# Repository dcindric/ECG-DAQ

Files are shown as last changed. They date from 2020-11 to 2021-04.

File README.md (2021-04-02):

# ECG-DAQ

<p align="justify">

ECG-DAQ is the data acquisition system for electrocardiogram signals. This project is built from scratch meaning that all that schematics and PCB is made by myself based on the reference designs, simulations and laboratory testing on prototypes. 

PCB is logically/phisically divided into two parts - precision analog section where input signals, coming from the electrodes (left and right arm, right leg), are conditioned and digital section used for signal processing and data transmission. 

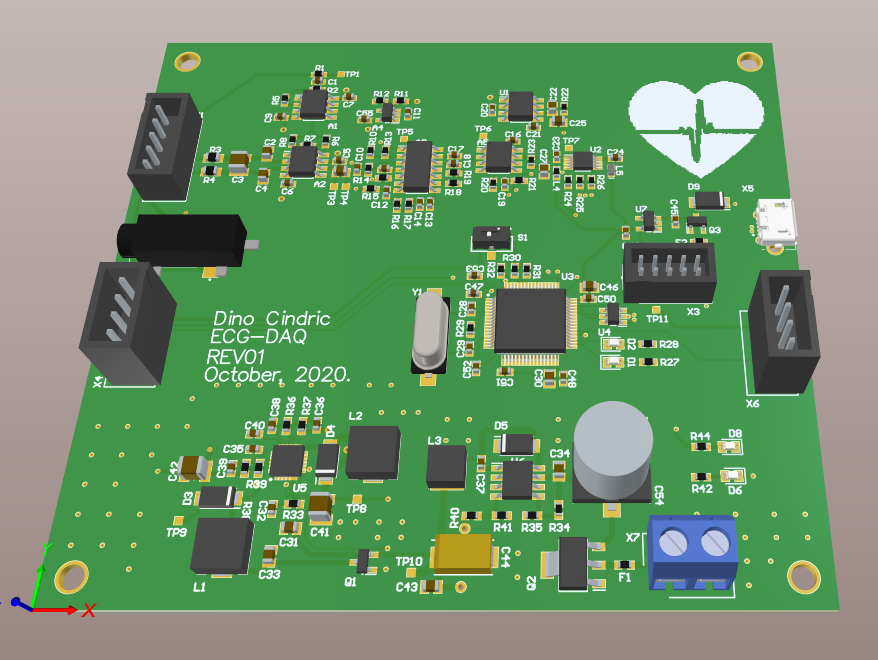
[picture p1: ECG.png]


Input signal conditioning includes:
* RFI/EMI differential filtering
* First gain stage using instrumentation amplifier INA818
* High-pass filtering implemented with 1st order C-R network 
* Second gain stage
* 5th order active Butterworth low-pass filter
* Precision ADC input preconditioning - voltage follower + antialiasing filtering
* ADCs voltage reference with driver circuit

Digital section is based on STM32F407 MCU and it's used for acquiring signals from ADC using 3-Wire SPI protocol, USB, I2C and UART communication with external devices and for executing various signal processing algorithms on acquired data (e.g. Pan-Tompkins). 

</p>

## Usage

Project files, including schematic and PCB documents, need to be opened with Altium Designer. Gerber files are production-ready and can be reviewed with various free alternative tools. 

**Disclaimer**: This project is work in progress. Use the files, hardware, and software given in this repository at your own risk.

## Updates
 * With power supply section completely soldered, negative voltage at TPS65130 regulator gave unstable, pulsating voltage, from -19 V up to -4 V.  The main reason for that behavior is that noise coupled into negative feedback pin (FBN) can be too large. This type of problem is well known for  this specific regulator and the solution is to add 51k resistor between C29 (16pF) capacitor and negative voltage rail. More discussion about this can be found here:
	* https://e2e.ti.com/support/power-management/f/power-management-forum/750348/tps65130-negative-supply-of-the-tps65130-is-not-regulating
	* https://e2e.ti.com/support/power-management/f/power-management-forum/727069/tps65130-inverting-converter-is-not-regulating-under-load
 * For some reason, I've received ADC's voltage reference driver opamp OPA2350 in wrong footprint. On the current prototyping board I've decided to solder TLV2376 opamp instead of OPA2350, since it's specifications should be good enough for ADC's voltage reference driver.
 * Initial testing of so-far-assembled board (only MCU section is not soldered yet) gave promising results.  More detailed test will be done after complete board assembly - basic functionalities of analog section are tested (signal amplification, filtering) and do perform well. Currently assembled parts of the board can be seen on the picture below.

**NOTE:** All component values and designators refer to ECG-DAQ schematic version 1.0, which can be found in Hardware/ProjectOutputs directory of this project.

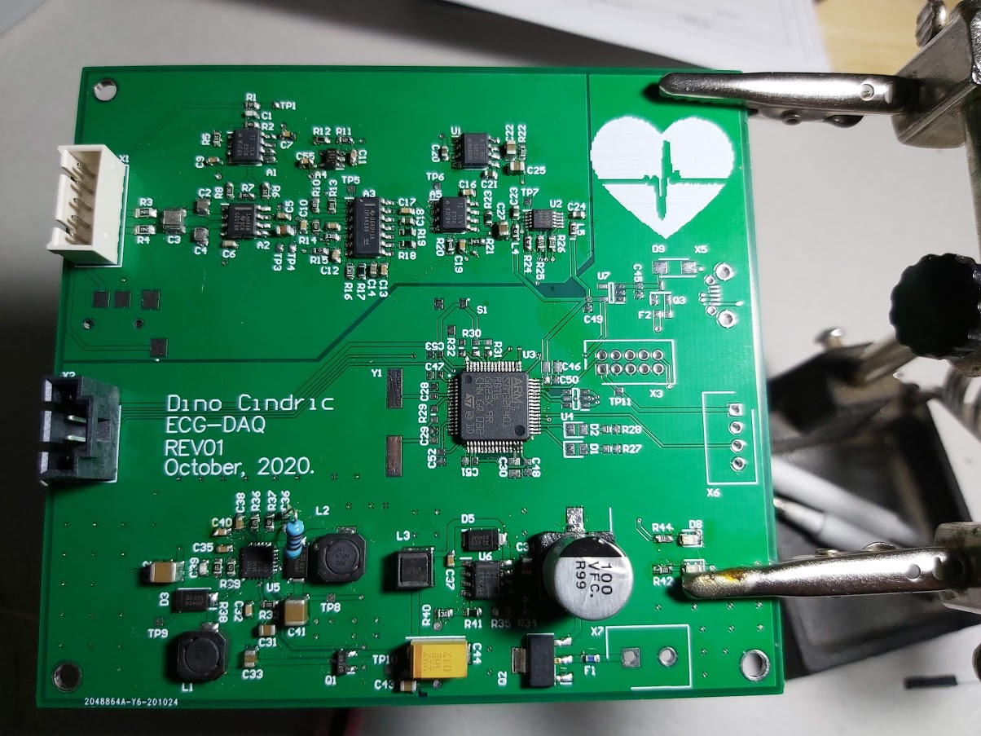
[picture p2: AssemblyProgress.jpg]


## Contributing
I'm currenlty writing firmware for the made PCB. It is very likely that there will be several versions of this project, so for any major or minor changes you would like to implement yourself, please open an issue so we can discuss about it or alternatively send me an email: dino.cindric@fer.hr.

Thank you.

## License
[MIT](https://choosealicense.com/licenses/mit/) Copyright (c) 2020, Dino Cindrić - All rights reserved.

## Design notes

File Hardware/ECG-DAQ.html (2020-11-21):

Altium customize

# Board Information Report

Date: | | 10/18/2020
Time: | | 4:13:02 PM
Elapsed Time: | | 00:00:00
Filename: | | C:\Users\Dino\Desktop\ECG Project\Schematic and PCB Design\ECG_DAQ\ECG-DAQ.PcbDoc
Units: | | mmmils

## Contents

Contents

Board Specification

General

Layer Information

Layer Information

## Board Specification

General
Board Size | 100mm x 91mm
Components on board | 146

Back to top

## Layer Information

Layer | Arcs | Pads | Vias | Tracks | Texts | Fills | Regions | ComponentBodies
Top Layer | 0 | 428 | 0 | 785 | 0 | 0 | 2 | 0
Int1 (GND) | 0 | 0 | 0 | 4 | 0 | 0 | 1 | 0
Int2 (PWR) | 0 | 0 | 0 | 4 | 0 | 0 | 1 | 0
Bottom Layer | 0 | 0 | 0 | 112 | 0 | 0 | 2 | 0
Mechanical 1 | 0 | 0 | 0 | 5 | 0 | 0 | 0 | 126
Dimensions | 0 | 0 | 0 | 16 | 2 | 0 | 0 | 0
Mechanical 13 | 0 | 0 | 0 | 570 | 0 | 0 | 0 | 10
Mechanical 15 | 0 | 0 | 0 | 542 | 0 | 0 | 0 | 0
Multi-Layer | 0 | 35 | 120 | 0 | 0 | 0 | 1 | 0
Top Paste | 0 | 0 | 0 | 0 | 0 | 0 | 0 | 0
Top Overlay | 7 | 0 | 0 | 196 | 292 | 0 | 0 | 0
Top Solder | 0 | 0 | 0 | 0 | 0 | 0 | 0 | 0
Bottom Solder | 0 | 0 | 0 | 0 | 0 | 0 | 0 | 0
Bottom Overlay | 0 | 0 | 0 | 0 | 0 | 0 | 0 | 0
Bottom Paste | 0 | 0 | 0 | 0 | 0 | 0 | 0 | 0
Drill Guide | 0 | 0 | 0 | 0 | 0 | 0 | 0 | 0
Keep-Out Layer | 0 | 0 | 0 | 6 | 0 | 0 | 0 | 0
Drill Drawing | 3 | 0 | 0 | 114 | 145 | 0 | 0 | 0
Total | 10 | 463 | 120 | 2354 | 439 | 0 | 7 | 136

Back to top

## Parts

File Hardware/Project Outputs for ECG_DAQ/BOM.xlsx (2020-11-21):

Comment | Designator | Quantity | Manufacturer Part Number 1
TLV2376IDR | A1 | 1 | TLV2376IDR
INA818IDR | A2 | 1 | INA818IDR
OPA4188IDR | A3 | 1 | OPA4188AIDR
OPA1671 | A4 | 1 | OPA1671IDBVR
OPA2350EA/2K5 | A5 | 1 | OPA2350EA/2K5
68p | C1 | 1 | C0603C680M5HACTU
680p | C2, C4 | 2 | ECH-U1H681GX5
22n | C3 | 1 | ECH-U1H223GX5
100n | C5, C6, C7, C9, C11, C12, C14, C15, C16, C18, C26, C32, C47, C48, C50, C51, C52, C53 | 18 | EMK107B7104KA-T, [NoValue]
6.8u | C8 | 1 | C2012X6S1C685M125AC
220p | C10 | 1 | VJ0603Y221KXJPW1BC
150n | C13 | 1 | CL10B154KO8NNNC
1u | C17, C20, C21, C45, C49 | 5 | EMK107BJ105KA-T
10n | C19, C35, C37 | 3 | C0603C103J4RACAUTO
10u | C22, C25, C27, C31, C33, C34, C43, C46 | 8 | EMK212BB7106KG-T
1uF | C23, C24 | 2 | EMK107BJ105KA-T
30p | C28, C29 | 2 | 06035U300FAT2A
2.2u | C30 | 1 | CL21B225KOFNNNE
16p | C36, C39 | 2 | AC0603JRNPO9BN160
220n | C38 | 1 | C0603C224J4RECTU
4.7n | C40 | 1 | C0603C472J5RACTU
22u | C41, C42 | 2 | TMK325B7226MMHP
220uF | C44 | 1 | TPSD227M016R0200V
RED | D1, D8 | 2 | LTST-C170CKT
GREEN | D2, D6 | 2 | LTST-C170KGKT
B340AF-13 | D3, D4, D5 | 3 | B340AF-13
YELLOW | D7 | 1 | LTST-C171YKT
B340A | D9 | 1
500mA | F1 | 1 | CC06FA500MA-TR
250mA | F2 | 1 | SF-0603FP025F-2
4.7uH | L1, L2 | 2 | B82462G4472M
18uH | L3 | 1 | SRR4828A-180M
SI2323DS-T1-GE3 | Q1, Q3 | 2 | SI2323DS-T1-GE3, [NoValue]
BSP321PH | Q2 | 1 | BSP321PH6327XTSA1
430k | R1, R37, R38 | 3 | CR0603-FX-4303ELF
750k | R2, R9 | 2 | CR0603-FX-7503ELF
2.4k | R3, R4 | 2 | ERJ-6ENF2401V
10k | R5, R6, R8, R14, R22, R32, R40 | 7 | RC0603FR-0710KL
4.64k | R7 | 1 | CR0603-FX-4641ELF
1k | R10 | 1 | RC0603FR-071KL
120k | R11, R36, R39 | 3 | CR0603-FX-1203ELF
100k | R12, R34, R35 | 3 | ERJ-3EKF1003V
39k | R13 | 1 | CR0603-FX-3902ELF
0Ω | R15 | 1 | ERJ-3GEY0R00V
6.34k | R16 | 1 | CRCW06036K34FKEA
9.76k | R17 | 1 | CRCW06039K76FKEA
2.43k | R18 | 1 | CRCW06032K43FKEA
3.74k | R19 | 1 | CRCW06033K74FKEA
4.7Ω | R20, R21 | 2 | CRCW06034R70FKEAC
0.1Ω | R23 | 1 | 560050316001
0Ω | R24 | 1 | ERJ-3GEY0R00V
47Ω | R25, R26 | 2 | CRCW060347R0JNEAC
2.0k | R27 | 1 | CRCW06032K00FKEA
1.8k | R28, R42, R43 | 3 | CRCW060311K8FKEA
47Ω | R29 | 1
4.7k | R30, R31 | 2 | CRCW06034K70FKEA
100Ω | R33 | 1 | CRCW0603100RFKEAC
3.24k | R41 | 1 | CRCW06033K24FKEA
2k | R44 | 1 | CRCW06032K00FKEA
CJS-1200TB | S1 | 1
REF5050 | U1 | 1 | REF5050AIDR
ADS8866IDGSR | U2 | 1 | ADS8866IDGSR
STM32F401RBT6 | U3 | 1 | STM32F401RBT6
USBLC6-2SC6 | U4 | 1 | USBLC6-2SC6
TPS65130 | U5 | 1 | TPS65130RGER
TPS5430DDAR | U6 | 1 | TPS5430DDAR
NCP115ASN330T2G | U7 | 1 | NCP115ASN330T2G
Pin Header | X1 | 1 | 35312-0560
3.5mm jack | X2 | 1 | SJ2-3574A-SMT-TR
SWD_CONN | X3 | 1 | 87831-1019
I2C_CONN | X4 | 1 | 171971-0004
USB Micro B | X5 | 1
UART_CONN | X6 | 1 | 171971-0004
VIN | X7 | 1 | 691111710002
8 MHz | Y1 | 1 | ECS-080-18-5PX-JES-TR

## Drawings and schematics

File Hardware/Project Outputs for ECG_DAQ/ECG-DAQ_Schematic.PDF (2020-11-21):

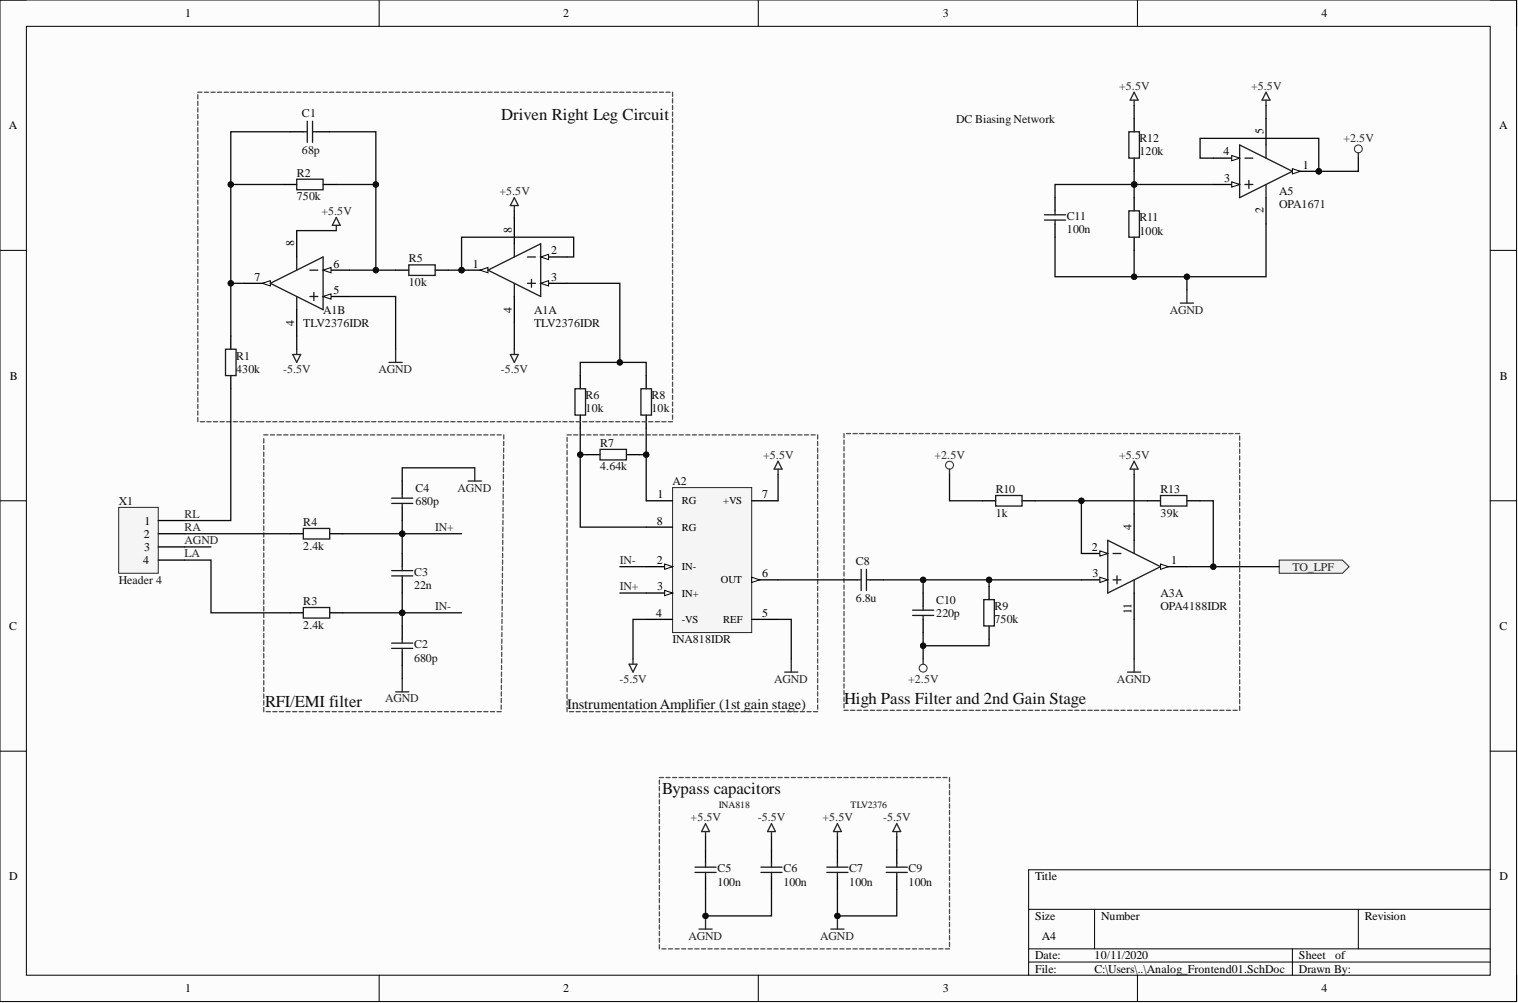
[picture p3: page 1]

Driven Right Leg Circuit

High Pass Filter and 2nd Gain Stage

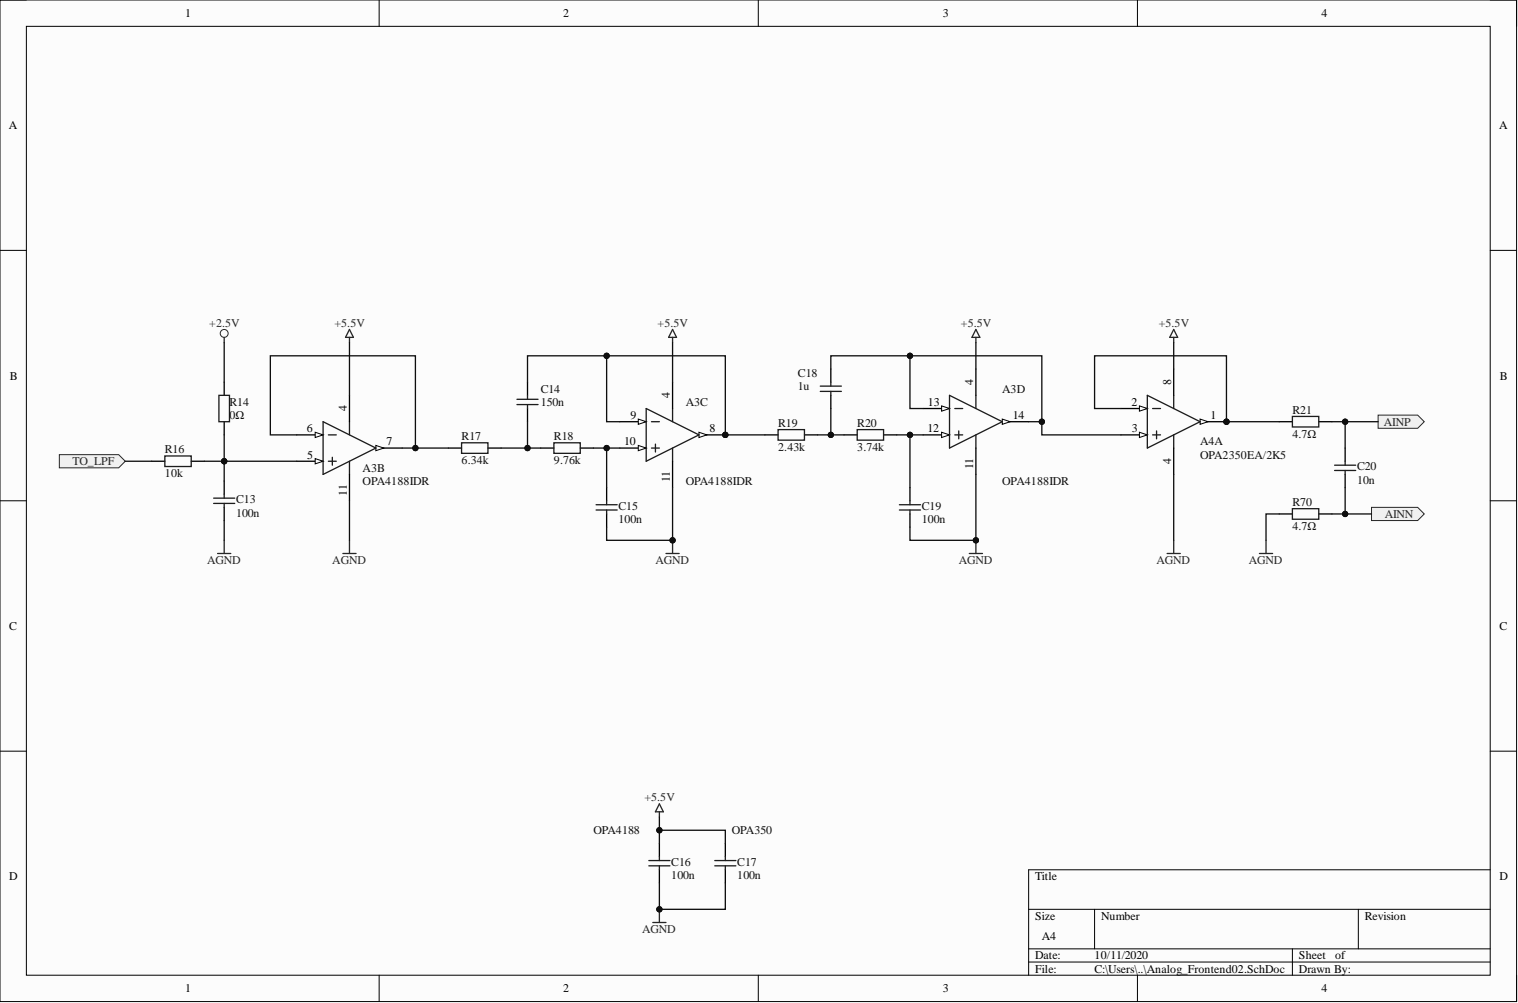
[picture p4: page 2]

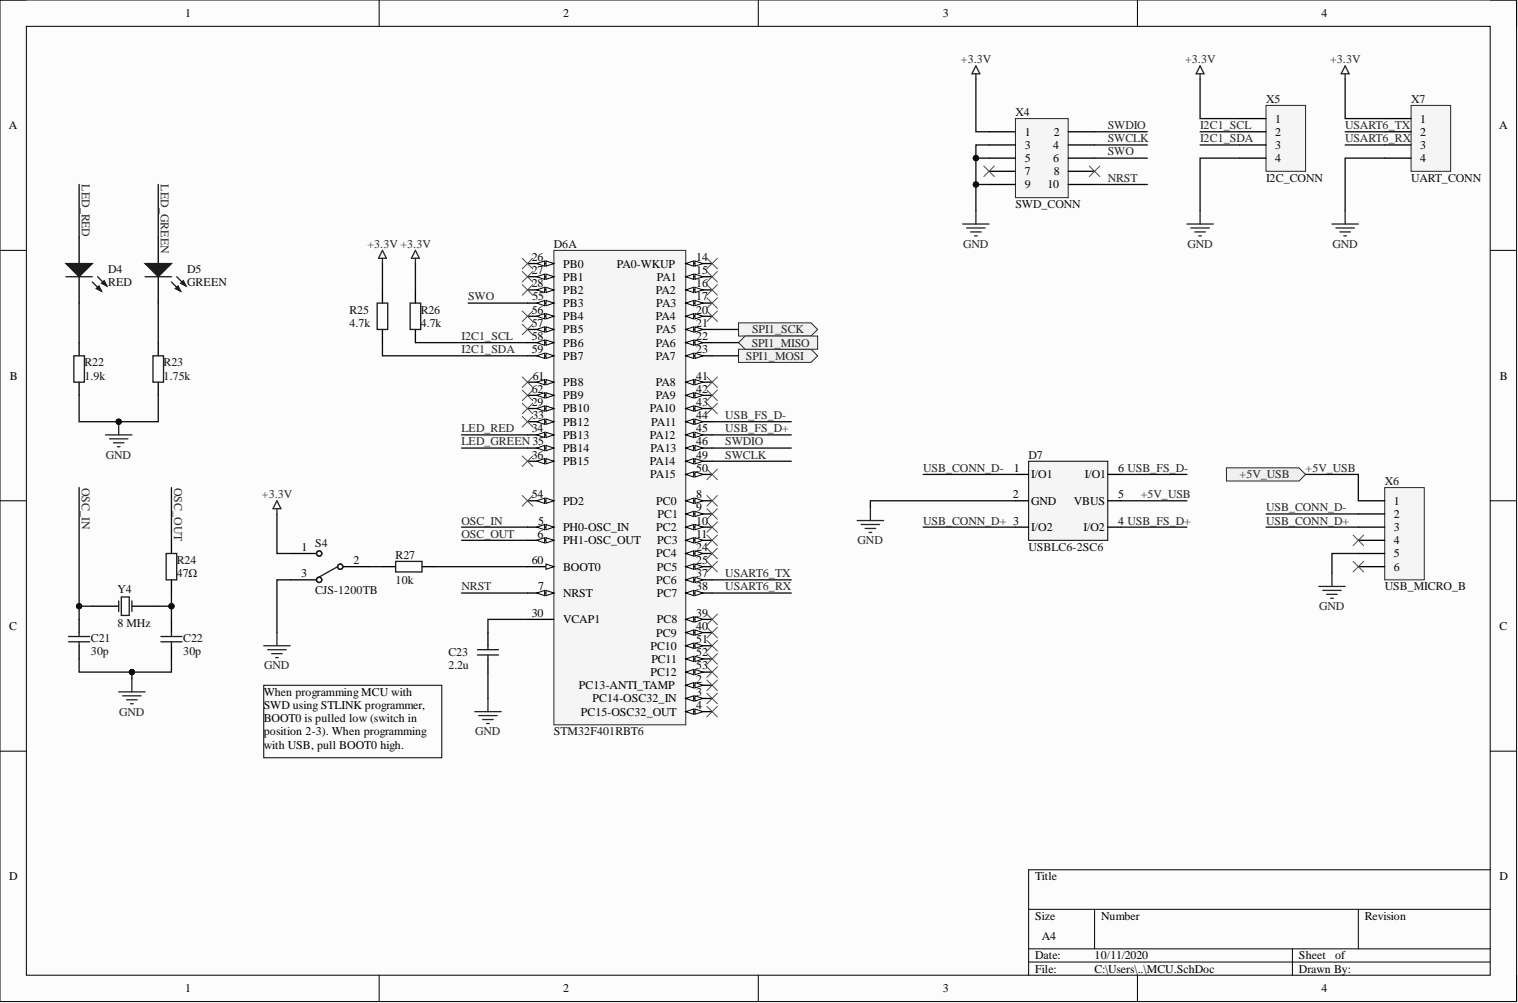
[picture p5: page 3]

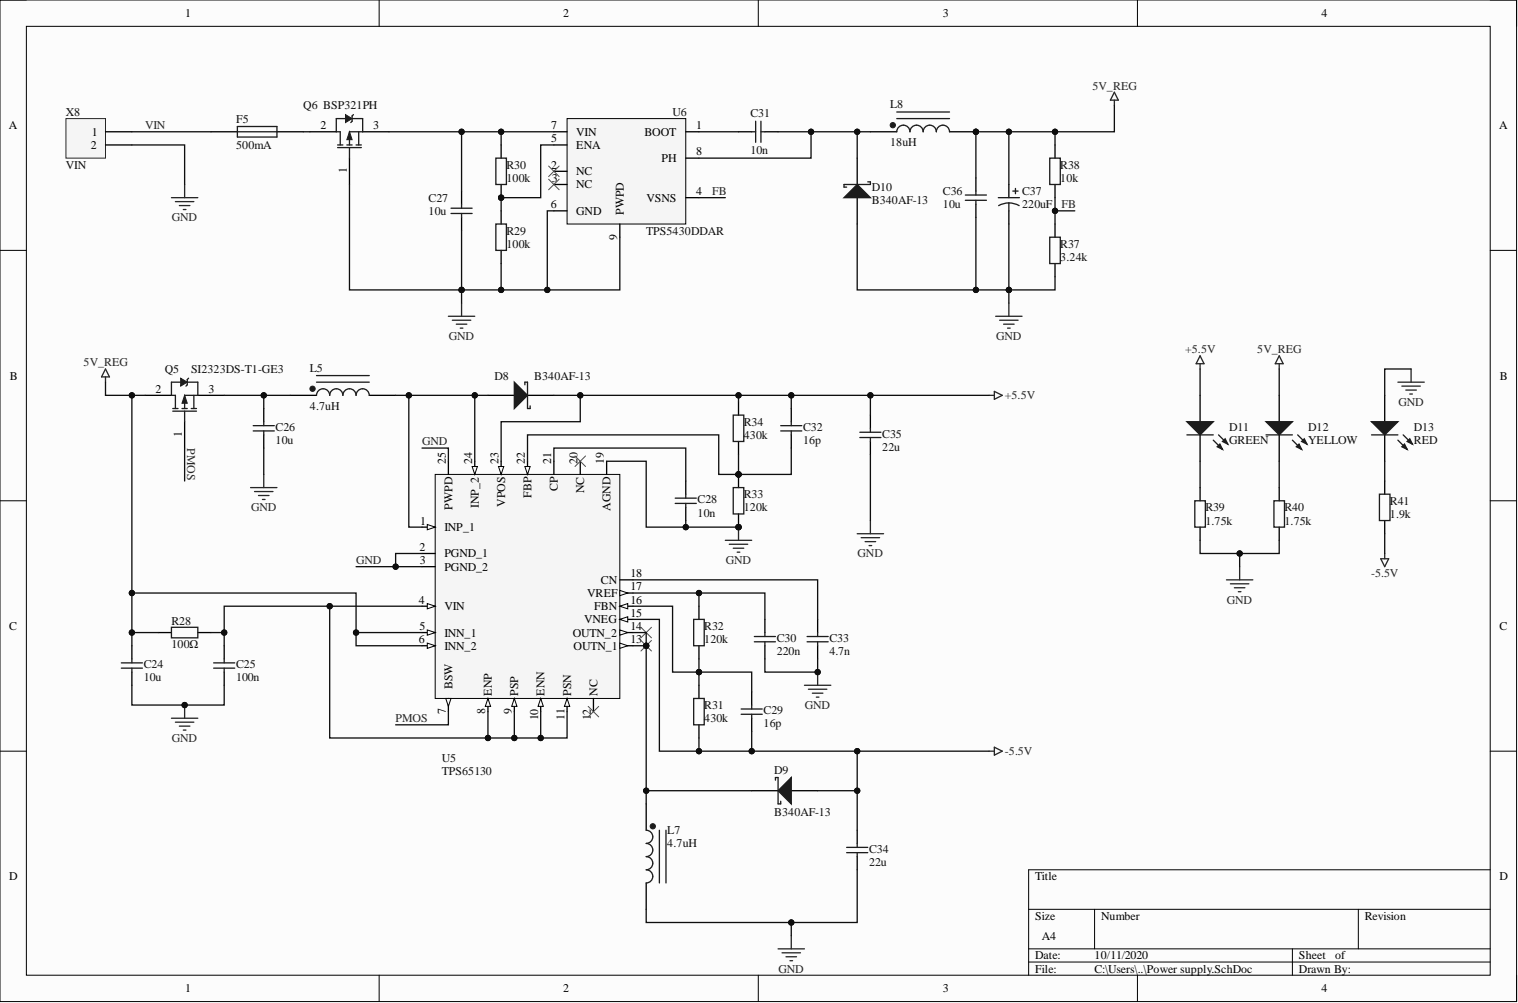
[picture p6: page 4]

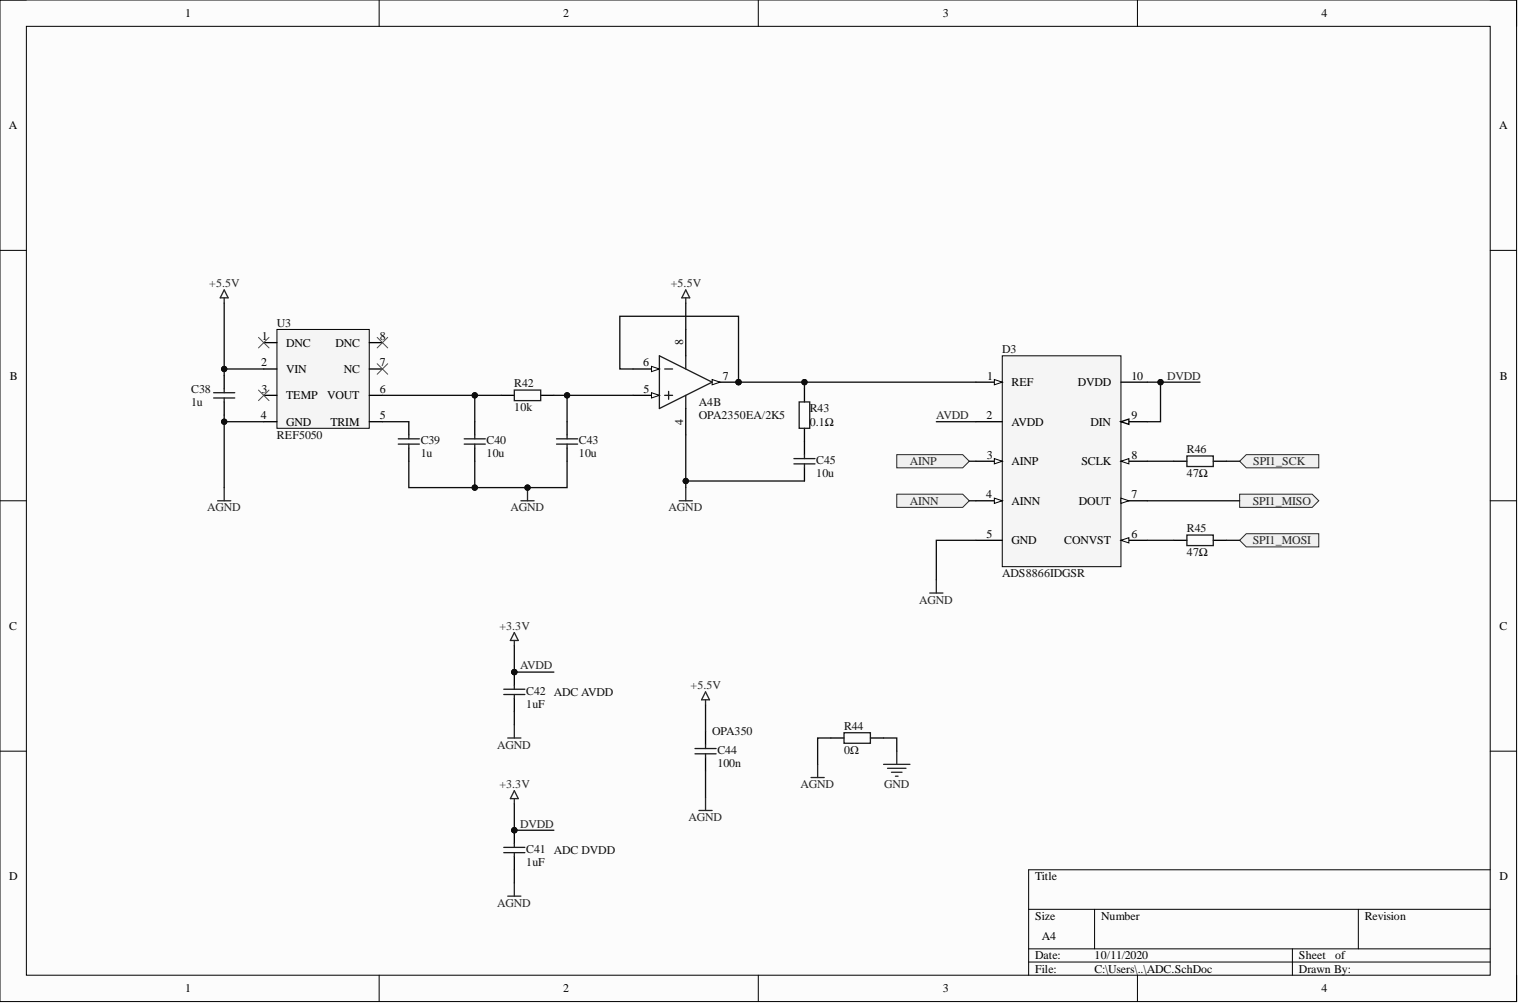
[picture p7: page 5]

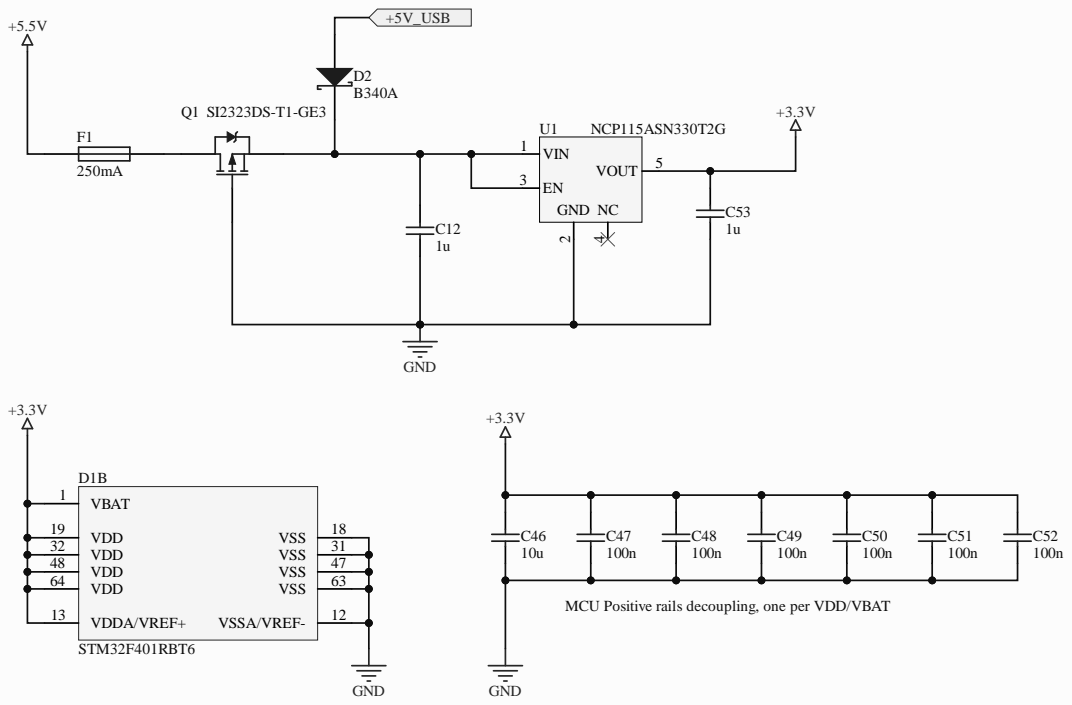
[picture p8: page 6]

MCU Positive rails decoupling, one per VDD/VBAT

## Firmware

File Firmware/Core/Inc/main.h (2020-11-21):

/* USER CODE BEGIN Header */
/**
  ******************************************************************************
  * @file           : main.h
  * @brief          : Header for main.c file.
  *                   This file contains the common defines of the application.
  ******************************************************************************
  * @attention
  *
  * <h2><center>&copy; Copyright (c) 2020 STMicroelectronics.
  * All rights reserved.</center></h2>
  *
  * This software component is licensed by ST under BSD 3-Clause license,
  * the "License"; You may not use this file except in compliance with the
  * License. You may obtain a copy of the License at:
  *                        opensource.org/licenses/BSD-3-Clause
  *
  ******************************************************************************
  */
/* USER CODE END Header */

/* Define to prevent recursive inclusion -------------------------------------*/
#ifndef __MAIN_H
#define __MAIN_H

#ifdef __cplusplus
extern "C" {
#endif

/* Includes ------------------------------------------------------------------*/
#include "stm32f4xx_hal.h"

/* Private includes ----------------------------------------------------------*/
/* USER CODE BEGIN Includes */

/* USER CODE END Includes */

/* Exported types ------------------------------------------------------------*/
/* USER CODE BEGIN ET */

/* USER CODE END ET */

/* Exported constants --------------------------------------------------------*/
/* USER CODE BEGIN EC */

/* USER CODE END EC */

/* Exported macro ------------------------------------------------------------*/
/* USER CODE BEGIN EM */

/* USER CODE END EM */

/* Exported functions prototypes ---------------------------------------------*/
void Error_Handler(void);

/* USER CODE BEGIN EFP */

/* USER CODE END EFP */

/* Private defines -----------------------------------------------------------*/
#define LED_RED_Pin GPIO_PIN_13
#define LED_RED_GPIO_Port GPIOB
#define LED_GREEN_Pin GPIO_PIN_14
#define LED_GREEN_GPIO_Port GPIOB
/* USER CODE BEGIN Private defines */

/* USER CODE END Private defines */

#ifdef __cplusplus
}
#endif

#endif /* __MAIN_H */

/************************ (C) COPYRIGHT STMicroelectronics *****END OF FILE****/
